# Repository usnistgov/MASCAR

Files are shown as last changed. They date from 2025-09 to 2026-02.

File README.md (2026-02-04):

# MASCAR
Assets and codebase for the Multi-Agent Synchronized Collaborative Assembly Replication (MASCAR) testbed.  This testbed was developed by the Collaborative Robotics Lab at the National Institute of Standards and Technology.

# Overview Video
View here:  https://youtu.be/IEJgwW6c2EQ

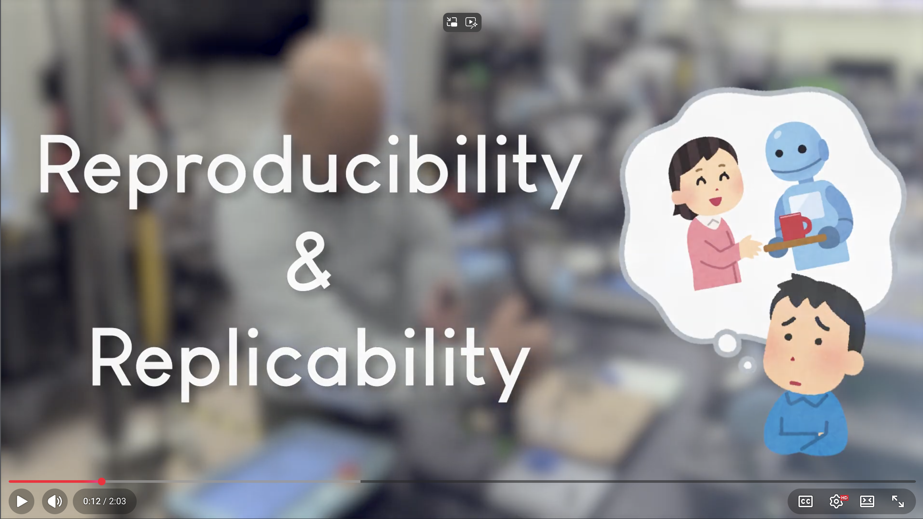
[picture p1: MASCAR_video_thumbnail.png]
MASCAR intro video (http://www.youtube.com/watch?v=IEJgwW6c2EQ "Introduction to MASCAR")


# Documentation
Please see our short paper in HRI 2026 for an overview:

[Local version](/HRI_2026_LBR%20-%20MASCAR.pdf)

[ACM Digital Library]() - Forthcoming

# Table of Contents
[CAD Files](/CAD%20Files/)
- [Testbed Components](/CAD%20Files/Testbed%20Components/)
    - [Cart and Tabletop](/CAD%20Files/Testbed%20Components/Cart%20and%20Tabletop/) - 
    Contains 2D and 3D models for recreation of the elements of the testbed, including the cart, surface mounting plates, and optical table tabletop design.
    - [Gripper Components](/CAD%20Files/Testbed%20Components/Gripper%20Components/) - Designs for yoke flange attached to the Robotiq 2F-85 for manual positioning and button control
    - [MoCap Marker Plates](/CAD%20Files/Testbed%20Components/MoCap%20Marker%20Plates/) - Models for attaching reflective mocap markers to the camera cold shoe mounts
    - [Raspberry Pi](/CAD%20Files/Testbed%20Components/Raspberry%20Pi/) - RP case models
    - 'NIST - Espressif ESP32-C3-DevKitC Case.stl' - Custom-designed case for ESP32
    - 'Laser_Diode_Holder.step' - 

[Design Documentation](/Design%20Documentation/)
- Diagrams, Bill of Materials, process description, design notes, and other instructions for running components of the testbed

[Safety](/Safety/)
- [Human Subjects Testbed](/Safety/Human%20Subjects%20Testbed/) - SOP for testbed setup & assembly
- [Universal Robots](/Safety/Universal%20Robots/) - Safety Manual for use of the UR3e

[Source Code](/Source%20Code/)
- [Python Code](/Source%20Code/Python%20Code/)) - Contains the code for controlling the Robotiq gripper via Raspberry Pi and UR RTDE, and the logger code for recording robot & gripper states
- [URCaps](/Source%20Code/URCaps/) - URCap program to be installed on UR3 for custom Robotiq gripper control

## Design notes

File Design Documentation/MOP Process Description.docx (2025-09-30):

# Teach-by-Demonstration Pilot Study

# (Pilot Testing Protocol)

Version 1.0

# Overview

This document outlines the process for executing a trial teach-by-demonstration data collection study. The study simulates a human subject trial in which a volunteer goes through the process of controlling a robot and its attached gripper to complete a sample assembly task. While the actual human subject study will leverage the NIST assembly taskboards, this assembly task is simplified to a pick-and-place operation of cubes into a grid. This simplification is for the sake of expediting the time necessary to complete the assembly.

The purpose of this study is to evaluate the efficacy of the testbed setup, data collection, and post-process data alignment and packaging.

# Training the Study Volunteer

Use the attached volunteer overview document to provide a convenient reference guide for the volunteer.

Provide a brief overview of robot safety, including the following points:

- Emergency stops
- Freedrive mode
- Joint limits and automatic deactivation

Provide a brief overview of the data being collected, including the following:

- Video of the volunteer operating the robot
- Point cloud data of the testbed environment, including the volunteer.
- Position and state data from the robot, which includes joint angles, Cartesian coordinates of the gripper, measured forces, etc.
- State data from the gripper, including button presses and aperture of the gripper.
- Screen recordings of the teach pendant.
- Time codes for each of the data streams.

Provide a brief summary of the controls for the robot.

- Demonstrate the gripper actuation
- Demonstrate freedrive mode
- Demonstrate picking up and putting down an object

Allow the study participant to practice controlling the robot and picking up and placing objects within the testbed. Reset the testbed prior to beginning the trial.

# Testbed Setup and Starting the Recording Process

Prior to starting the testing process, set up the staging area with the five cubes. Each cube goes into a specific slot on the staging area fixture:

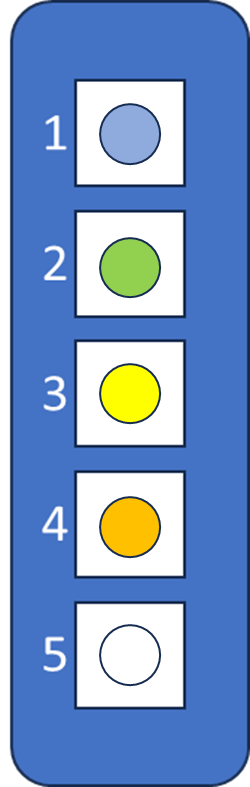
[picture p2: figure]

Blue: Slot 1 Green: Slot 2 Yellow: Slot 3 Orange: Slot 4 White: Slot 5

The 5x5 target grid should be empty of all blocks.

The robot’s J6 should be oriented such that the gripper control flange is pointed to the side with the participant’s dominant hand (left or right).

A second tester must be present to provide emergency services, including being stationed with an emergency stop button to stop the robot in the event of dangerous motions.

# Teach-By-Demonstration Process Description

The volunteer will be instructed to control the robot using the on-arm button interface to pick up and place cubes in a specific order.

When the participant is ready, start recording for all data streams.

For each pick-and-place operation, provide a card stating which cube is to be picked up, and the 2-digit location of the target receptacle of the block. Give the participant only one card at a time, and provide the next card only after the current object has been placed.

# Teach-by-Demonstration Pilot Study

# (Volunteer Reference Sheet)

# Safety

Before beginning the test, please familiarize yourself with the safety functions of the robotic testbed.

An emergency stop button (large red button with an orange and black base) is provided for your benefit. If at any time the robot or its actions make you feel unsafe, press the red button and the robot will stop immediately. Stopping the robot in this manner requires a manual restart (the button must be manually released, and the robot re-enabled to allow it to move again), so it is impossible for the robot to automatically restart itself.

During the trials, one of the testers will also be watching the robot’s actions, and will have their own, separate emergency stop button. This tester’s singular responsibility is to ensure your safety.

The robot also constantly monitors its functional state, and will disable itself if aberrant actions are detected. Aberrant actions include:

- Moving faster than a set, maximum speed,
- Rapid acceleration (including impacts)
- Excessive force, and
- Encountering physical joint limits (the robot’s joints cannot be turned infinitely due to hardware limitations).
- Encountering virtual position limits (the robot may be configured to prevent it moving beyond certain position thresholds; e.g., attempting to move below the table surface)

While working with the robot, it is recommended you tie back any loose hair or clothing to prevent accidentally being snagged on the robot, its gripper, or the various parts in the testbed. Keep hands, hair, and clothing away from the gripper while it is opening or closing. Although commanded forces have been reduced to prevent injury, it may be startling or slightly uncomfortable if you get pinched.

All sensitive or personal equipment (jewelry, name badges, etc.) should be removed prior to beginning the trial. A bin will be provided to deposit these materials.

# Task Overview

During this study, your task will be to move cubes from a staging area (left column) to specific locations on the target board (right grid). You will be instructed which block to move from the staging area using its numerical position in the column, and where on the grid to move the block using its column and row combination. Each block will have a colored indentation on the top, but this is not relevant to this test.

For example, you may be asked to move block #2 to position E1 on the grid, in which case you will use the robot to pick up the block from the staging area in space 2 (second from the top), and then move it to location E1 (top right square) on the grid. While each block will have a color associated with it, these colors are not part of this test.

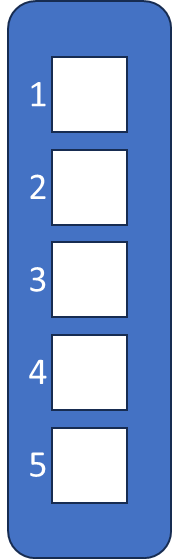
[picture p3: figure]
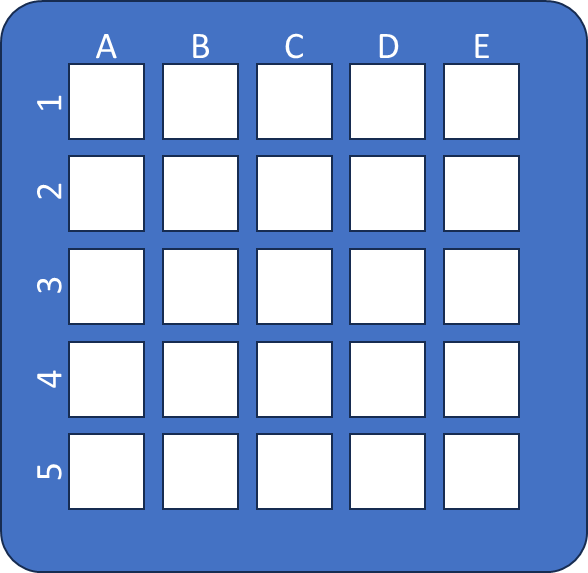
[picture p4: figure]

The order of the pick-and-place operations does matter, so please try to do each action in the order it is given to you.

Note that you will not be allowed to correct erroneous placement of objects. Simply move on to the next object.

The duration of the test will be timed. However, the goal of this test is to evaluate task accuracy, and not to determine how quickly you can complete it.

Additional measurements that will be recorded include:

- Video and audio of the test,
- Point cloud data (i.e., a series of dots in three dimensions that show where the surfaces of people and objects are in the environment)
- Task accuracy as a percentage of maximum number of correct placements, and as a measure of order of operations,
- Robot and gripper joint configurations,
- Gripper location,
- Incurred forces and torques, and
- Button presses

# Robot Controls

For this experiment, you will be controlling the robot manually by means of a button interface attached to the robot’s gripper. The interface consists of a collar attached to the robot, just above a robotic gripper. The protrusion with the buttons is double-sided, and has an identical button layout on the opposite side.

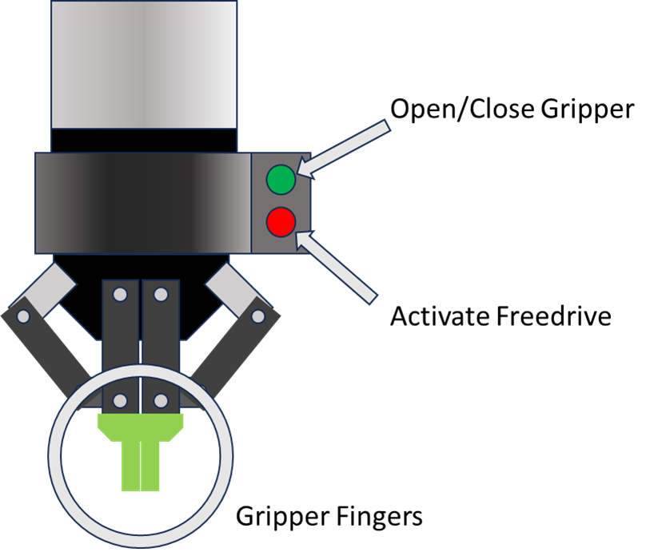
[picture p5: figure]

The top buttons (green) control the gripper, and cycle between “open” (the green “fingers” are spread apart) and “closed” (the green fingers are close together). To actuate the gripper, simply simultaneously press the two green buttons on both sides of the gripper, hold for about half a second, and then release. If the gripper is open, this will close it; and if the gripper is closed, it will open it again.

The bottom buttons (red) enable the robot’s “freedrive” mode. In freedrive mode, the brakes release and the robot will allow you to push and pull it into different joint configurations. While in freedrive mode, the robot is active, and is interpreting the forces you are applying to it as motion commands. Pressing and holding the red buttons will enable freedrive mode. Freedrive mode will remain active while both buttons are pressed. Releasing the buttons will disable freedrive, and the robot’s brakes will engage again.

The following instructions are recommended to ensure smooth operations:

- When using freedrive mode, hold the gripper with both hands to provide the maximum level of control.
- Do not attempt to move the robot quickly. Completion time is not part of this test.

# Teach-by-Demonstration Pilot Study

# (Subject Information and Informed Consent Form)

A sample test methodology for subject data collection as part of a new research testbed for human-robot interaction.

Qualified investigator: Megan Zimmerman

Sub-investigator(s): Jeremy Marvel and Shelly Bagchi

Introduction:

You are being invited to participate in a research study (also known as a “test” or “trial”). This research is part of a pilot, and will focus on the collection of data for the verification and validation of a testing methodology and is not part of a larger human subject study. The data collected will be used to evaluate and calibrate the processes for disparate data stream synchronization and alignment.

Including the time necessary to explain the purpose of this study (including training, reading the reference materials and this consent form, and conducting the teach-by-demonstration trial) is expected to take no longer than 30 minutes.

It is your choice if you want to participate in this study.

This form explains why we are conducting this study, the nature of the data being collected, and how this data is being stored and protected.

What is the purpose of this study?

The purpose of this study is to generate test data for the evaluation of the methodologies of data collection, data synchronization, and automated data segmentation and analysis. The research questions being addressed are:

Are the processes of collecting data accurate and repeatable?

What is the uncertainty of the data alignment methodology?

Is the collection of sensors meaningful for the evaluation of human-robot interaction?

Who can take part in this study?

To take part in this study, you must be at least 18 years of age, be able to see objects in the environment with or without visual aids, have full functionality of at least one arm and hand, and be able to listen to and understand instructions presented in English.

What will we ask you to do?

You will be trained to use an industrial robot with a simplified interface to simulate a teach-by- demonstration programming process. Following this, you will be asked to complete a series of five (5) pick-and-place operations using a small industrial robot, guided by hand, with a robotic gripper controlled using buttons attached to the robot. You will be instructed on the order of the objects to pick up, and where to place them on a grid.

Risks and discomforts

Physical risk: The robot and its gripper are controlled manually and at a reduced speed. It is possible, however, that study participants could get pinched by the gripper or caught between the robot and the test surface. Minor bruising may be possible under such circumstances.

Security risk: This pilot study includes the use of video equipment with which the face or other personally identifiable physical features of the participant may be recorded. All data collected during this study will be securely stored on a password-protected drive, and are to be used only for internal purposes (i.e., no data containing personally-identifiable information will be publicly released).

Benefits

Participation in this study will produce valuable data that will be used to validate and fine-tune the testing protocols, that will, in turn, be used as bases for establishing standards for human-robot interaction research as part of the IEEE P3108 committee on recommended practices for human-robot interaction.

If you have questions

If you have any questions following this study, or would like to know more about the resulting collected data, please contact Megan Zimmerman, Computer Scientist in the NIST Intelligent Systems Division. You may ask questions now, or contact Megan at megan.zimmerman@nist.gov. You may also request a copy of this consent form by contacting Megan at the above address.

Statement of Consent

I have read the above information, and have received answers to any questions I asked. I consent to take part in the study and have my likeness recorded for the purpose of test protocol verification.

Your Signature: ____________________________________________

Your Name (printed): _________________________________________

Date: _____________________________________

Signature of person obtaining consent: ____________________________________________

Printed name of person obtaining consent: _________________________________________

Date: _____________________________________

This consent form will be kept by the researcher for at least three (3) years beyond the end of the study.

# Teach-by-Demonstration Pilot Study

# (Testing Scenarios)

# Scenario 1:

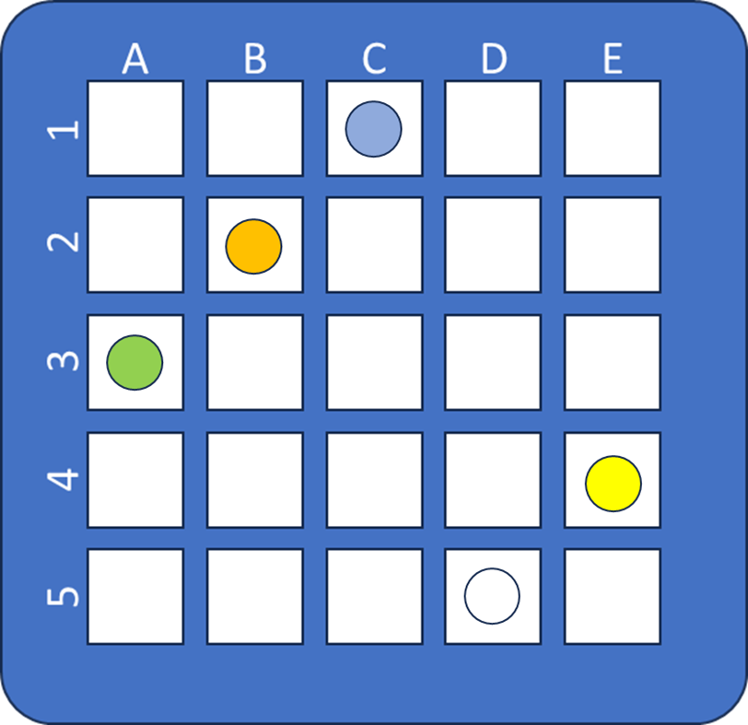
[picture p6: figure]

| Block
| 1 | 2 | 3 | 4 | 5
Target Location | C1 | A3 | E4 | B2 | D5

# Scenario 2:

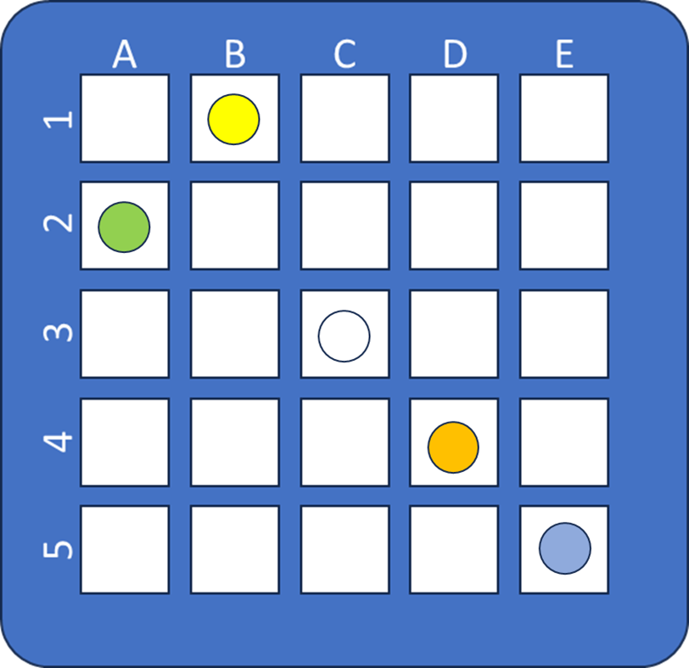
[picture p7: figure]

| Block
| 1 | 2 | 3 | 4 | 5
Target Location | E5 | A2 | B1 | D4 | C3

# Scenario 3:

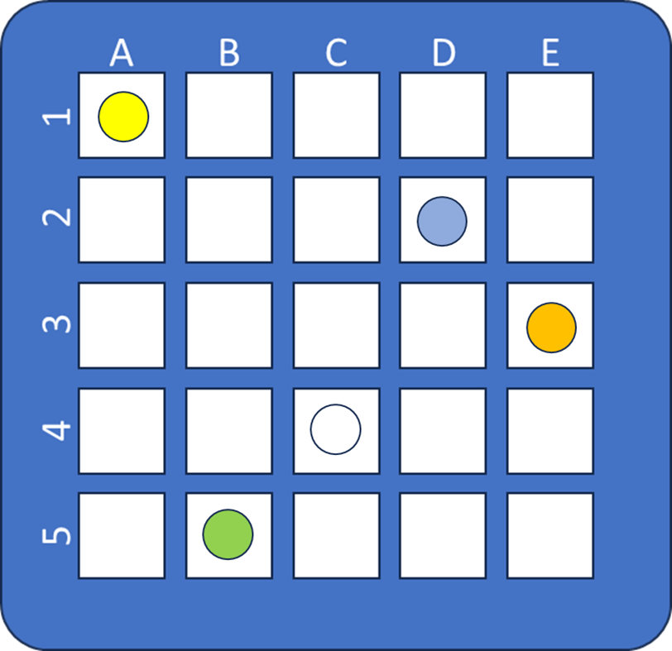
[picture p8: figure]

| Block
| 1 | 2 | 3 | 4 | 5
Target Location | D2 | B5 | A1 | E3 | C4

# Scenario 4:

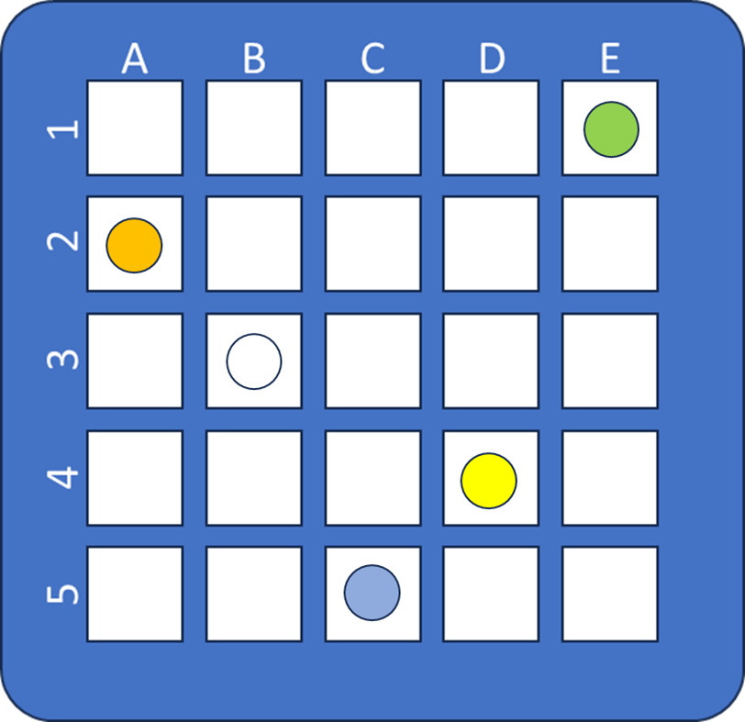
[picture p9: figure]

| Block
| 1 | 2 | 3 | 4 | 5
Target Location | C5 | E1 | D4 | A2 | B3

# Scenario 5:

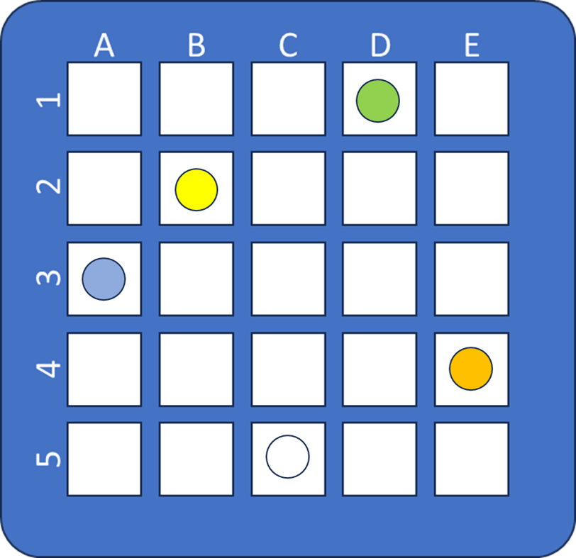
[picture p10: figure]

| Block
| 1 | 2 | 3 | 4 | 5
Target Location | A3 | D1 | B2 | E4 | C5

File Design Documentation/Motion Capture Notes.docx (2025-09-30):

Motion Capture SOP Notes

OptiTrack Duo and Trio

If the intrinsic calibration of the cameras is not loading correctly (e.g., if the cameras appear to be co-located, or are not triangulating markers correctly), it can be manually forced to load using the following steps:

With the camera powered on and connected to the computer via USB:

- From the “Edit” menu, select “Reset Settings.” This will force a reload of the camera definition, effectively placing the cameras in the approximate correct position.
- Then, in the “Ground Plane” window, select “Change Ground Plane” and then in the ground plane editing window, select “Reset.” This will force the intrinsic calibration to reload, correcting any potential errors in camera offsets and orientations.

To set the ground plane and define the origin of the coordinate space:

Using three retroreflective markers, create an “L” shape pattern on the surface of the ground plane. The long segment of the “L” defines the positive Z axis, and the short segment defines the positive X axis

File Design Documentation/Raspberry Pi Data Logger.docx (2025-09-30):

Raspberry Pi 2B

Button: 1 lead to GPIO, 1 to GND

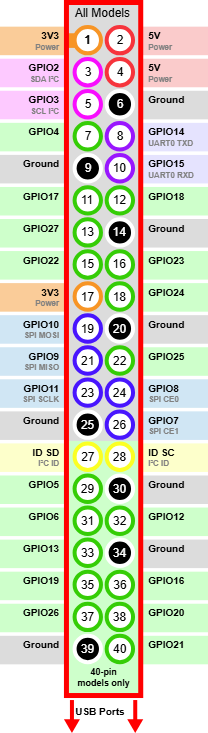
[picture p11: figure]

Raspberry Pi 5

1x USB3.0 port: SSD for data output

1x USB2.0 port: Audio in for timecode generator

1x RJ45 Ethernet port to connect to LAN for access to UR3e & Gripper server

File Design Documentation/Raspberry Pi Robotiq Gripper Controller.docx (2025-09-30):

# Raspberry Pi Control of Robotiq Grippers

Version 1.0

23 April, 2025

Last edited by: Jeremy Marvel (jeremy.marvel@nist.gov)

# Introduction

This transcript documents the process for setting up a Raspberry Pi as a remote triggering device for opening and closing a Robotiq gripper. The original intention of this process was to enable manual control of the gripper using a simple button press. The source code registers any button press longer than 0.5s as a “press event” to prevent unintentional actuation, and each press event will alternatively open and close the gripper.

The methods described in this document have been tested on both the 3-fingered Modbus Ethernet gripper, as well as the 2-fingered RS485 serial gripper.

# Bill of Materials

NOTE: Bill of Materials does not include the cost of the gripper or associated cables. Instead, it reflects only the materials needed to control the gripper with a Raspberry Pi.

Item | Quantity | Example Link & Cost
Raspberry Pi 3B | 1 | $35.00 (https://www.adafruit.com/product/3055)
4GB MicroSD Card | 1 | $8.49 (https://www.amazon.com/SanDisk-microSDHC-Memory-SDSDQ-004G-Packaging/dp/B00FM1JGHK/?th=1)
Normally-open momentary switch | 1 | $8.99 (package of 20) (https://www.amazon.com/MTDELE-Momentary-Button-Switch-Normally/dp/B0D7ZYZN58/)
24VDC 10A power supply | 1 | $22.99 (https://www.amazon.com/ALITOVE-Transformer-Universal-Regulated-Switching/dp/B078RYWZMH?th=1)
5V 3A micro USB power supply (for the Raspberry Pi) | 1 | $9.99 (https://www.amazon.com/Listed-iUniker-Raspberry-Supply-Switch/dp/B0B79FVPQ4/)
22 Gauge wire (for wiring the button) | 2 spools | $15.20 (package of 2) (https://www.amazon.com/BINNEKER-Gauge-Electric-Tinned-Copper/dp/B0B19HJFPX/?th=1)
Network switch | 1 | $13.95 (https://www.amazon.com/Ethernet-Splitter-Optimization-Unmanaged-TL-SG105/dp/B00A128S24?th=1)
RJ45 CAT5 Network Cable | 1 | $9.99 (https://www.amazon.com/Cable-Matters-Snagless-Ethernet-Black/dp/B007NZGPAY/?th=1)

OR
USB to RS485 adapter | 1 | $15.35 (https://www.amazon.com/Industrial-USB-RS485-Converter-Communication/dp/B081MB6PN2/)
Modbus Ethernet | | $124.60
USB to RS485 | | $116.01

# Wiring a Button to a Raspberry Pi

For this setup, we use normally open (NO) momentary switches, with one lead connected to the GPIO pin 2 on the Raspberry Pi, and the other lead connected to the GND pin. For the NIST application, two NO momentary switches were wired in series to force the operator to press and hold both buttons for 0.5s to trigger the gripper actuation.

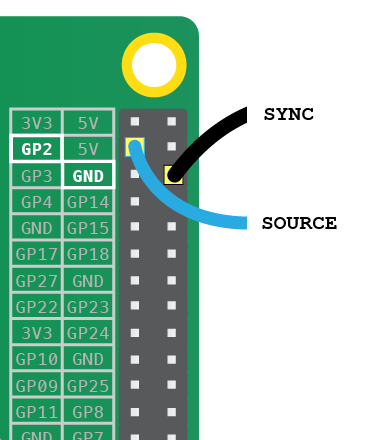
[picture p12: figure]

# Modbus over Ethernet (Robotiq 3-Finger Gripper)

Installation of the Python libraries

python3 -m pip config set global.break-system-packages true

python3 -m pip install pyModbusTCP

SOURCE

from pyModbusTCP.client import ModbusClient

from gpiozero import Button

import time

import threading

import warnings

class GripperController:

def __init__(self, server_ip, port=502, unit_id=9, update_interval=0.1):

# Initialize Modbus client and update thread

self.client = ModbusClient(host=server_ip, port=port, auto_open=True, unit_id=unit_id)

self.client.open()

self.update_interval = update_interval

self._running = True

self._thread = threading.Thread(target=self._update_loop)

self._thread.start()

def _update_loop(self):

"""Continuously update gripper status."""

while self._running:

self._update_status()

time.sleep(self.update_interval)

def _update_status(self):

"""Update and store the gripper status from Modbus server."""

readData = self.client.read_input_registers(0,8)

if readData:

self.gSTA, self.gIMC, self.gGTO, self.gMOD, self.gACT, self.gDTS, self.gDTC, self.gDTB, self.gDTA = self.stat(self.add_leading_zeros(bin(readData[0])))

self.FaultStatus, self.FingerA_PositionReqEcho = self.Byte_status(self.add_leading_zeros(bin(readData[1])))

self.FingerA_Position, self.FingerA_Current = self.Byte_status(self.add_leading_zeros(bin(readData[2])))

self.FingerB_PositionReqEcho, self.FingerB_Position = self.Byte_status(self.add_leading_zeros(bin(readData[3])))

self.FingerB_Current, self.FingerC_PositionReqEcho = self.Byte_status(self.add_leading_zeros(bin(readData[4])))

self.FingerC_Position, self.FingerC_Current = self.Byte_status(self.add_leading_zeros(bin(readData[5])))

self.Scissor_PositionReqEcho, self.Scissor_Position = self.Byte_status(self.add_leading_zeros(bin(readData[6])))

self.Scissor_Current, RES = self.Byte_status(self.add_leading_zeros(bin(readData[7])))

else:

print("Error reading data in update_status.")

@staticmethod

def add_leading_zeros(bin_num, total_length=16):

"""Ensure binary number string has correct number of digits."""

bin_str = str(bin_num)[2:] # remove '0b' prefix

return bin_str.zfill(total_length)

@staticmethod

def Byte_status(variable: int) -> str:

"""Split and parse byte status."""

B1 = int(variable[0:8],2)

B2 = int(variable[8:16],2)

return B1, B2

@staticmethod

def stat(variable: int) -> str:

"""Split and parse status."""

# Define gripper modes

modes = ["Basic Mode", "Pinch Mode", "Wide Mode", "Scissor Mode"]

# Split and parse status bits

gSTA = int(variable[0:2],2)

gIMC = int(variable[2:4],2)

gGTO = int(variable[4],2)

gMOD = int(variable[5:7],2)

gMOD = modes[gMOD] # Translate mode code to string

gACT = int(variable[7],2)

gDTS = int(variable[8:10],2)

gDTC = int(variable[10:12],2)

gDTB = int(variable[12:14],2)

gDTA = int(variable[14:16],2)

return gSTA, gIMC, gGTO, gMOD, gACT, gDTS, gDTC, gDTB, gDTA

def activate(self):

"""Activate the gripper."""

# response = self.client.write_multiple_registers(0, [self._action_req_variable(rACT=1), 0, 0])

self.client.write_multiple_registers(

0,

[self._action_req_variable(rACT=1, rGTO=1, rMOD=0, rICF=0),

self._position_req_variable(0),

self._write_req_variable(0, 0)]

)

print("Gripper activate")

time.sleep(1)

def command_gripper(self, rPRA=[1, 1, 1], rSP=[250, 250, 250], rFR=[250, 250, 250], rMOD="Basic", rICF=False):

"""Send a command to the gripper."""

# self.status()

modes = {"Basic": 0, "Pinch": 1, "Wide": 2, "Scissor": 3}

rMOD = modes[rMOD]

if rICF:

for var in [rPRA, rSP, rFR]:

if isinstance(var, int):

self.close()

raise ValueError("Input variables must be 3d vectors when using Individual Control Flag.")

response = self.client.write_multiple_registers(

0,

[self._action_req_variable(rACT=1, rGTO=1, rMOD=rMOD, rICF=1),

self._position_req_variable(rPRA[0]),

self._write_req_variable(rSP[0], rFR[0]),

self._write_req_variable(rPRA[1],rSP[1]),

self._write_req_variable(rFR[1],rPRA[2]),

self._write_req_variable(rSP[2], rFR[2]),]

)

else:

for var in [rPRA, rSP, rFR]:

if isinstance(var, list):

warnings.warn("only first value of 3d vector will be used when not using Individual Control Flag.")

response = self.client.write_multiple_registers(

0,

[self._action_req_variable(rACT=1, rGTO=1, rMOD=rMOD, rICF=0),

self._position_req_variable(rPRA[0]),

self._write_req_variable(rSP[0], rFR[0])]

)

def status(self):

readData = self.client.read_input_registers(0,8)

if readData:

self.gSTA, self.gIMC, self.gGTO, self.gMOD, self.gACT, self.gDTS, self.gDTC, self.gDTB, self.gDTA = self.stat(self.add_leading_zeros(bin(readData[0])))

self.FaultStatus, self.FingerA_PositionReqEcho = self.Byte_status(self.add_leading_zeros(bin(readData[1])))

self.FingerA_Position, self.FingerA_Current = self.Byte_status(self.add_leading_zeros(bin(readData[2])))

self.FingerB_PositionReqEcho, self.FingerB_Position = self.Byte_status(self.add_leading_zeros(bin(readData[3])))

self.FingerB_Current, self.FingerC_PositionReqEcho = self.Byte_status(self.add_leading_zeros(bin(readData[4])))

self.FingerC_Position, self.FingerC_Current = self.Byte_status(self.add_leading_zeros(bin(readData[5])))

self.Scissor_PositionReqEcho, self.Scissor_Position = self.Byte_status(self.add_leading_zeros(bin(readData[6])))

self.Scissor_Current, RES = self.Byte_status(self.add_leading_zeros(bin(readData[7])))

else:

print("Error reading data in status.")

def _action_req_variable(self, rARD: int = 0, rATR: int = 0, rGTO: int = 0, rACT: int = 0, rMOD:int = 0, rICS:int = 0, rICF:int = 0 ) -> str:

"""Build action request variable."""

# Check if the input variables are either 0 or 1

for var in [rARD, rATR, rGTO, rACT]:

if var not in [0, 1]:

raise ValueError("Input variables must be either 0 or 1.")

rMOD = bin(rMOD).replace("0b", "").zfill(2)

# Construct the string variable

string_variable = f"0b00{rARD}{rATR}{rGTO}{rMOD}{rACT}0000{rICS}{rICF}00"

return int(string_variable,2)

def _position_req_variable(self, rPR: int = 0) -> str:

"""Build position request variable."""

# Check if the input variables are between 0 or 255

for var in [rPR]:

if var not in range(0,256):

raise ValueError("Input variables must be between 0 and 255.")

rPR = format(rPR, '08b')

# Construct the string variable

string_variable = f"0b00000000{rPR}"

return int(string_variable,2)

def _write_req_variable(self, X: int = 0, Y: int = 0) -> str:

"""Build write request variable."""

# Check if the input variables are between 0 to 255

for var in [X, Y]:

if var not in range(0,256):

raise ValueError("Input variables must be between 0 and 255.")

X = format(X, '08b')

Y = format(Y, '08b')

# Construct the string variable

string_variable = f"0b{X}{Y}"

return int(string_variable,2)

def close(self):

"""Stop the update thread and close the Modbus client."""

self._running = False

self._thread.join()

self.client.close()

print("Connection closed.")

# @brief Main program loop

def main():

# Create and activate gripper controller

while ([gripper.FingerA_Position, gripper.FingerB_Position, gripper.FingerC_Position] != target_position):

print(f"FingerA_Position: {gripper.FingerA_Position}")

print(f"FingerA_Position: {gripper.FingerA_Position}")

gripper = GripperController("169.254.116.11")

gripper.activate()

individual_control = False

target_position = [255, 255, 255] # Desired finger positions

speed = [250, 205, 250] # Speed of the movement

force = [250, 250, 250] # Force applied by the fingers

target_position = [target_position[0]] * 3 if not individual_control else target_position

startTime_ = time.perf_counter()

stopTime_ = time.perf_counter()

state = False

time.sleep (0.2)

# Send command to gripper and wait for it to reach final position

target_position = [255, 255, 255]

gripper.command_gripper(rPRA=target_position, rSP=speed, rFR=force, rICF=individual_control)

button = Button(2)

while True:

button.wait_for_press()

startTime_ = time.perf_counter()

button.wait_for_release()

stopTime_ = time.perf_counter()

elapseTime_ = stopTime_ - startTime_

if elapseTime_ > 0.5:

state = not state

if state:

target_position = [0, 0, 0]

else:

target_position = [0, 0, 0]

gripper.command_gripper(rPRA=target_position, rSP=speed, rFR=force, rICF=individual_control)

if __name__ == "__main__":

main()

There are two known issues regarding the use of the Raspberry Pi4B for communicating with the Robotiq grippers over Ethernet; one is a hardware issue, and the other is an OS setting issue when running Raspian based on the Debian GNU/Linux 12 (Bookworm) kernel.

Hardware Issue:

The Pi4B requires an Ethernet cable with all 8 pins of the RJ45 plug connected and wired accordingly.

OS Setting Issue:

By default, the Raspberry Pi4B requires a router that can either set DHCP IP addresses, or “confirm” the static IP address of the Pi. Even if you set a static IP address, the OS will keep “trying” to establish a connection with the LAN, despite that it is visible to other machines on the LAN and can likewise see those other machines. Eventually the OS times out on establishing this connection, and disables the RJ45 port until a new connection is detected.

To bypass this verification step for a static IP address, use the following instructions:

Setting a static IP address (Network Settings (icon on the top-right corner of the desktop) → Advanced Options → Edit Connections)

- Double-click “Wired connection 1”
- Under the “General” tab
  - Set “Connect automatically with priority” to 100 (default is -999)
  - Set “Metered connection” to No
- Under “IPv4 Settings” tab
  - Set “Method” to Manual
  - Add a new static IP address and netmask based on the LAN you are setting up
  - Make sure “Require IPv4 addressing for this connection to complete” is NOT checked (otherwise OS will eventually shut it off since a network switch/hub will not provide verification of IP address)
- Under “IPv6 Settings” tab
  - Set “Method” to Disabled
- Click “Save” button and exit

# USB to RS485 Serial (Robotiq 2-Finger Gripper)

Controlling the 2-finger Robotiq gripper is substantially easier, as communications between the Raspberry Pi and the gripper is handled via an RS485 interface.

Installation of the Python libraries

python3 -m pip config set global.break-system-packages true

python3 -m pip install pyRobotiqGripper

python3 -m pip install minimalmodbus

Wiring and Installation

From the Robotiq documentation:

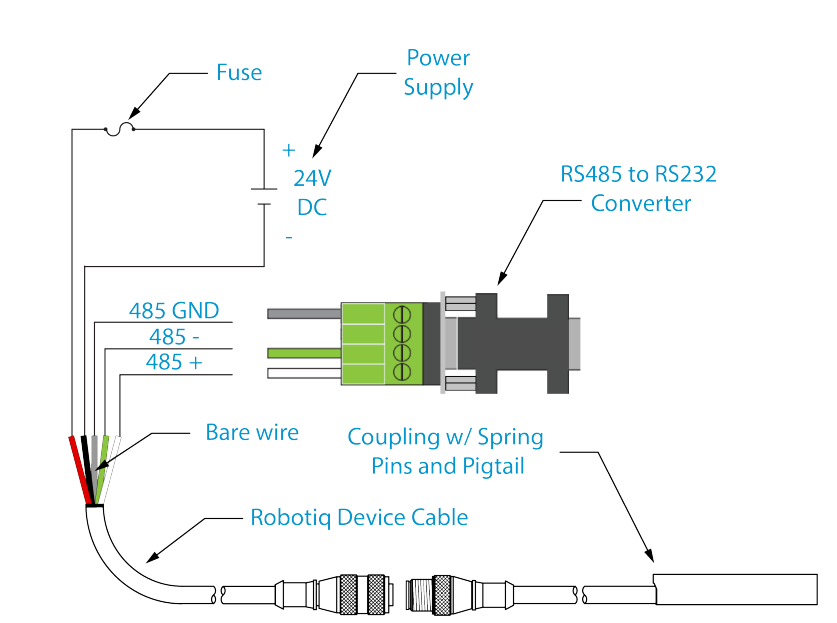
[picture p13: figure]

Our configuration did not use an RS232 - RS485 converter, but instead used a USB - RS485 adapter. The wiring at the RS485 side remained the same.

SOURCE

from gpiozero import Button

import pyRobotiqGripper

import time

# @brief Main program loop

def main():

gripper = pyRobotiqGripper.RobotiqGripper()

gripper.activate()

startTime_ = time.perf_counter()

stopTime_ = time.perf_counter()

state = False

time.sleep (0.2)

gripper.close()

button = Button(2)

while True:

button.wait_for_press()

startTime_ = time.perf_counter()

button.wait_for_release()

stopTime_ = time.perf_counter()

elapseTime_ = stopTime_ - startTime_

if elapseTime_ > 0.5:

state = not state

if state:

gripper.open()

else:

gripper.close()

if __name__ == "__main__":

main()

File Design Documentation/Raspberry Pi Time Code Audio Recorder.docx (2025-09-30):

# Recording Time Code Generator Audio using a Raspberry Pi

Version 1.0

23 August, 2025

Last edited by: Jeremy Marvel (jeremy.marvel@nist.gov)

Installation of the Python library

python3 -m pip install pyaudio

https://people.csail.mit.edu/hubert/pyaudio/docs/

PyAudio library

https://people.csail.mit.edu/hubert/pyaudio/docs/

# @brief Launch and run in a new thread the audio recorder

# =============================================================================================================

def timecode_recorder():

form_1 = pyaudio.paInt16 #! 16-bit resolution

chans = 1 #! 1 channel

samp_rate = 44100 #! 44.1 kHz sampling

chunk = 4096 #! 4k samples for buffer

global running_

global recording_

global timestr_

global index_

global timeRec_

#! Create the Python audio instantiation

audio = pyaudio.PyAudio()

print ("Opening audio on device index " + str(index_))

stream = audio.open(format = form_1, rate = samp_rate, channels = chans,\

input_device_index = index_, input = True, \

frames_per_buffer = chunk)

stream.stop_stream()

stream.close()

#! Loop until told by the main program function to quit

while running_:

if recording_:

timeRec_ = True

print ("Recording time code data")

stream = audio.open(format = form_1, rate = samp_rate, channels = chans,\

input_device_index = index_, input = True, \

frames_per_buffer = chunk)

wavfilename = timestr_ + "_audio.wav"

frames = []

#! Loop until told by the main program function to stop recordng

while recording_:

data = stream.read(chunk)

frames.append(data)

print ("Finalizing time code data log")

stream.stop_stream()

stream.close()

wavfile = wave.open(wavfilename, 'wb')

wavfile.setnchannels(chans)

wavfile.setsampwidth(audio.get_sample_size(form_1))

wavfile.setframerate(samp_rate)

wavfile.writeframes(b''.join(frames))

wavfile.close()

print("Finished writing timecode file")

timeRec_ = False

print("Timecode recorder quitting...")

audio.terminate()

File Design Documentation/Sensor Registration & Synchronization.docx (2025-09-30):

Calibration

Sensor | Intrinsic Calibration | Extrinsic Calibration
Camcorder | N/A | Coordinate space registration using an artifact with OptiTrack markers. Sensor uses a custom routine to track an object in its intrinsic coordinate system, while the OptiTrack tracks the pose of the sensor and the artifact. Calculate the transformation from the sensor’s coordinate space to the OptiTrack coordinate space using the NIST registration method.
Intel RealSense | Pre-calibrated | Coordinate space registration using an artifact with OptiTrack markers. Sensor uses a custom routine to track an object in its intrinsic coordinate system, while the OptiTrack tracks the pose of the sensor and the artifact. Calculate the transformation from the sensor’s coordinate space to the OptiTrack coordinate space using the NIST registration method.
Audio | N/A | OptitTrack marker
Captury MoCap | Built-in setup routine per camera | Built-in setup routine between cameras and with the measurement space
OptiTrack MoCap | Pre-calibrated | N/A; Built-in setup routine with the measurement space.
Vicon MoCap | Built-in setup routine per camera | Built-in setup routine between cameras
UR Teach Pendant | Occasional confirmation of robot pose on startup | N/A currently (Probably could put on OptiTrack markers)
Forge/OS Teach Pendant | N/A | N/A currently (Probably could put on OptiTrack markers)
UR UR3e robot | DH parameters; built-in calibration routine at startup | Intrinsic design of the testbed mounting points
Robotiq robotic gripper | Built-in calibration routine at startup | Manual TCP offset on teach pendant
Control collar | N/A | N/A currently

Registration

Sensor | Data Format | Spatial Registration | Temporal Synchronization
Camcorder | AVI video and embedded 2-channel audio | Attached OptiTrack marker | Time code generator
Intel RealSense | | Attached OptiTrack marker
Audio | WAV | Attached OptiTrack marker | Time code generator
Captury MoCap | AVI video and tracking data | Modification of the calibration target to include MoCap markers to register with the OptiTrack and/or Vicon
OptiTrack MoCap | Tracking data
Vicon MoCap | Tracking data
UR Teach Pendant | AVI video
Forge/OS Teach Pendant | AVI video
UR UR3e robot | RTDE data stream
Robotiq robotic gripper | | Physically attached to the UR3e tool flange
Control collar | | Physically attached to the Robotiq gripper

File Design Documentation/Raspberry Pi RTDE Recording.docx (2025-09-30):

# Recording Universal Robot Manipulator State Via the RTDE on a Raspberry Pi

Version 1.0

15 August, 2025

Last edited by: Jeremy Marvel (jeremy.marvel@nist.gov)

Guide is available at https://www.universal-robots.com/articles/ur/interface-communication/real-time-data-exchange-rtde-guide/

Download latest release from https://www.github.com/UniversalRobots/RTDE_Python_Client_Library/releases

Installation of the Python library:

python3 -m pip config set global.break-system-packages true

python3 -m pip install ./rtde-<version>-release.zip

# @brief Launch and run in a new thread the UR RTDE recorder

# ======================================================================

def rtde_recorder():

global running_

global recording_

global timestr_

global UR3Rec_

verbose = True

host = "169.254.152.41" #! TODO: Replace with IP address of UR controller

port = 30004

freq = 125

binary = False

if verbose:

logging.basicConfig(level=logging.INFO)

conf = rtde_config.ConfigFile("logger.xml")

output_names, output_types = conf.get_recipe("out")

#! Connect to the robot controller

con = rtde.RTDE(host, port)

con.connect()

#! Get controller version

con.get_controller_version()

#! Set up recipes

if not con.send_output_setup(output_names, output_types, frequency=freq):

logging.error("Unable to configure output")

sys.exit()

#! Start data synchronization

if not con.send_start():

logging.error("Unable to start synchronization")

sys.exit()

writeModes = "wb" if binary else "w"

while running_:

if recording_:

rtdefilename = timestr_ + "_rtde.csv"

rtdetimefile = timestr_ + "_rtde_timestamps.csv"

with open (rtdetimefile, writeModes) as rtdetime:

with open(rtdefilename, writeModes) as csvfile:

writer = None

UR3Rec_ = True

if binary:

writer = csv_binary_writer.CSVBinaryWriter(csvfile, output_names, output_types)

else:

writer = csv_writer.CSVWriter(csvfile, output_names, output_types)

print ("Recording UR3 state data")

writer.writeheader()

#! Loop until instructed to stop by the main program

while recording_:

try:

#state = con.receive_buffered(binary)

state = con.receive(binary) #! Only get the most recent message

if state is not None:

timstr = datetime.datetime.now()

writer.writerow(state)

rtdetime.writerow(timestr)

except rtde.RTDEException:

con.disconnect()

sys.exit()

UR3Rec_ = False

print("Finished writing UR3 log file")

# with open(rtdefilename, writeModes) as csvfile

#! with open() automatically closes the file when completed

# with open (rtdetimefile, writeModes) as rtdetime:

print ("Finalizing UR3 timestamp log")

# while running_

#! Close the connection to the robot controller

con.send_pause()

con.disconnect()

# ======================================================================

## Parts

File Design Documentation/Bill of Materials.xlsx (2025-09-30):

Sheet: Master
 | Cost
Hardware | $51764.27
Robot Control Handle | $34.55
ForgeOS Modifications | $78.43
Computers | $41152.63
Markerless Motion Capture | $33273.62
RPi Gripper Controller | $151.67
RPi Robot Logger | $88.49
Sensors | $9324.57
Task Boards | 0
Total | $135868.23

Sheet: Hardware
Part number | Item description | Link | Cost per unit | Quantity | Total | Note | Total cost: | $51764.27
UR3-e | Universal Robot UR3-E robot with 3kg lift capacity |  | $26995.00 | 1 | $26995.00
Forge/OS | Robot controller interface with multi-robot support |  | $9750.00 | 1 | $9750.00
2-finger adaptive gripper | Robotiq 85mm adaptive, 2-finger gripper for UR e-series robots |  | $5885.00 | 1 | $5885.00
Table base | Wheeled workbench base with hand-crank for height adjustment | https://www.mcmaster.com/3517T81/ | $1771.25 | 1 | $1771.25
Table top V1 | 1/2" thick plywood sheet, painted green, with a self-leveling epoxy finish to provide a level surface | https://www.homedepot.com/p/ProWood-1-2-in-x-2-ft-x-4-ft-BCX-Sanded-Plywood-109119/202093833 | $21.23 | 1 | $21.23 | Price reflects only cost of the plywood sheet, and does not include the paint or epoxy resin
Table top V2 | Machined aluminum table top with 6mm tapped holes for attaching parts and a pre-drilled mounting pattern for the e-series robot |  | $4912.00 | 1 | $4912.00 | Machined at the NIST shops. Price reflects material and labor costs.
Table top V3 | Machined aluminum table top with 6mm tapped holes for attaching parts and a pre-drilled mounting pattern for the e-series robot |  |  | 1 | $0.00 | Machined at the NIST shops. Price reflects material and labor costs.
Rack cabinet | 8U equipment rack cabinet | https://www.bhphotovideo.com/c/product/1260039-REG/auray_ers_8u_ers_8u_steel_equipment.html (https://gcc02.safelinks.protection.outlook.com/?reserved=0) | $139.95 | 1 | $139.95
Shelf material |  |  |  | 2 | $0.00
Shelf support |  |  |  | 3 | $0.00
GFW-ID-CREATORTREE | A/V armatures | https://www.bhphotovideo.com/c/product/1657199-REG/gator_gfw_id_creatortree_frameworks_id_series_all_in_one.html (https://gcc02.safelinks.protection.outlook.com/?reserved=0) | $208.41 | 2 | $416.82
Ergotron 24206214 | Computer cart | https://www.bhphotovideo.com/c/product/1128696-REG/ergotron_neo_flex_24_206_214_lcd_cart.html (https://gcc02.safelinks.protection.outlook.com/?reserved=0) | $1075.00 | 1 | $1075.00
JB01741 | Tablet mount | https://www.bhphotovideo.com/c/product/1675875-REG/joby_jb01741_griptight_tablet_pro_2.html (https://gcc02.safelinks.protection.outlook.com/?reserved=0) | $48.66 | 1 | $48.66
955-000005 | Table-mounted camera stand | https://www.bhphotovideo.com/c/product/1585609-REG/mevo_mv3_11a_bl_table_stand.html (https://gcc02.safelinks.protection.outlook.com/?reserved=0) | $65.99 | 1 | $65.99
Neewer C-Stand with Extension Arm |  | Neewer C-Stand with Extension Arm 66600020 B&H Photo Video (https://www.bhphotovideo.com/c/product/1732647-REG/neewer_66600020_pure_metal_pro_reflector.html) | $102.34 | 5 | $511.70
Sandbags | Neewer Heavy-Duty Sandbags for Light Stands, Boom Stands & Tripods (6-Pack) | Neewer Heavy-Duty Sandbags for Light Stands, Boom Stands (https://www.bhphotovideo.com/c/product/1732696-REG/neewer_66600134_dual_handle_sandbag_6_pack.html) | $25.47 | 1 | $25.47
 |  |  |  | 10 | $0.00
Floor cable trays | Cable Concealment Ramp Track | Auray CBR-1039 Cable Concealment Ramp Track CBR-1039 B&H Photo (https://www.bhphotovideo.com/c/product/1585966-REG/auray_cbr_1039_cable_concealment_ramp_10.html) | $29.24 | 5 | $146.20
 |  |  |  |  | $0.00
 |  |  |  |  | $0.00
 |  |  |  |  | $0.00
 |  |  |  |  | $0.00
1/4-20 to 3/8-16 adapters |  |  |  |  | $0.00
M6 female to M4 male adapter |  |  |  |  | $0.00
 |  |  |  |  | $0.00
 | Light panels |  |  |  | $0.00
 |  |  |  |  | $0.00
 |  |  |  |  | $0.00
 |  |  |  |  | $0.00
 |  |  |  |  | $0.00
 |  |  |  |  | $0.00

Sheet: Robot Control Handle
Part number | Item description | Link | Cost per unit | Quantity | Total | Note | Total cost: | $34.55
 | Normally-open momentary switch | https://a.co/d/glXAlmD | $11.49 | 1 | $11.49
 | Latching switches | https://www.digikey.com/en/products/detail/cw-industries/GPB023B05BR/2235499 | $3.93 | 2 | $7.86
 | Aluminum yoke structure |  | $0.00 | 1 | $0.00 | Raw material. Custom machined at NIST.
 | Handles |  | $0.00 | 1 | $0.00 | 3D printed @NIST
 | 22 Gauge wire (for wiring the button) | https://www.amazon.com/BINNEKER-Gauge-Electric-Tinned-Copper/dp/B0B19HJFPX/?th=1 | $15.20 | 1 | $15.20
 | Sheathing |  | $0.00 | 1 | $0.00
 |  |  | $0.00 | 1 | $0.00
 |  |  |  | 1 | $0.00
 |  |  |  | 1 | $0.00
 |  |  |  |  | $0.00

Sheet: ForgeOS Modification
Part number | Item description | Link | Cost per unit | Quantity | Total | Note | Total cost: | $78.43
 | LVDS to HDMI adapter | https://geekworm.com/products/lvds-to-hdmi-adapter-board-converter-with-lvds-cable?variant=39521988771928 | $35.00 | 1 | $35.00
 | LVDS to HDMI adapter | https://geekworm.com/products/lvds2 | $35.00 | 1 | $35.00
2073-05-40-D-0254-A-4-06-4-T-ND | 40-pin FPC ribbon cable | https://mou.sr/3MWxTQ2 (https://gcc02.safelinks.protection.outlook.com/?url=https%3A%2F%2Fmou.sr%2F3MWxTQ2&reserved=0) | $1.43 | 1 | $1.43
1528-4905-ND | 40-pin FPC ribbon cable to 2x20 IDC adapter | https://mou.sr/47GDsMf (https://gcc02.safelinks.protection.outlook.com/?url=https%3A%2F%2Fmou.sr%2F47GDsMf&reserved=0) | $3.50 | 2 | $7.00
 |  |  |  |  | $0.00
 |  |  |  |  | $0.00
 |  |  |  |  | $0.00
 |  |  |  |  | $0.00
 |  |  |  |  | $0.00
 |  |  |  |  | $0.00
 |  |  |  |  | $0.00
 |  |  |  |  | $0.00
 |  |  |  |  | $0.00
 |  |  |  |  | $0.00
 |  |  |  |  | $0.00
 |  |  |  |  | $0.00
 |  |  |  |  | $0.00
 |  |  |  |  | $0.00
 |  |  |  |  | $0.00
 |  |  |  |  | $0.00
 |  |  |  |  | $0.00
 |  |  |  |  | $0.00
 |  |  |  |  | $0.00
 |  |  |  |  | $0.00
 |  |  |  |  | $0.00
 |  |  |  |  | $0.00
 |  |  |  |  | $0.00
 |  |  |  |  | $0.00
 |  |  |  |  | $0.00
 |  |  |  |  | $0.00
 |  |  |  |  | $0.00
 |  |  |  |  | $0.00
 |  |  |  |  | $0.00

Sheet: Computers and Peripherals
Part number | Item description | Link | Cost per unit | Quantity | Total | Note | Total cost: | $41152.63
Dell Precision 5860 | Desktop computer |  | $12367.78 | 3 | $37103.34
Dell Latitude 7350 | Detachable tablet computer |  | $2315.02 | 1 | $2315.02
 |  |  |  | 1 | $0.00
Monitor |  |  |  | 1 | $0.00
Keyboard |  |  |  | 1 | $0.00
Mouse |  |  |  | 1 | $0.00
BG-UHD-KVM41A | BZBGEAR 4-Port HDMI KVM Switch | https://www.bhphotovideo.com/c/product/1660951-REG/bzbgear_bg_uhd_kvm41a_4x1_kvm_switcher_with.html | $128.00 | 1 | $128.00
Networking switch |  |  |  | 1 | $0.00
Black Lion PG-2 | 120VAC Power conditioner & surge protector |  | $399.00 | 1 | $399.00
USB Audio Line In Adapter |  | https://a.co/d/gPL7H8t | $19.09 | 2 | $38.18
Blackmagic Design ATEM Mini Extreme ISO |  |  | 1169.09 | 1 | 1169.09
 |  |  |  |  | $39983.54

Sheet: Markerless Motion Capture
Part number | Item description | Link | Cost per unit | Quantity | Total | Note | Total cost: | $33273.62
Captury Studio | Software for markerless motion capture |  | $8000.00 | 1 | $8000.00
Netgear M4300-16X | 16-port 10Gb POE Network Switch | https://www.bhphotovideo.com/c/product/1711406-REG/netgear_xsm4316pa_100nes_m4300_16x_stackable_managed_switch.html | $2399.99 | 1 | $2399.99
111297 | 25' 10G network cables | https://www.amazon.com/Monoprice-Entegrade-Cat6a-Ethernet-Patch/dp/B00KWS6VIU/?th=1 | $17.98 | 9 | $161.82
BFS-PGE-13Y3C-C | 1.3 MP POE Color Camera | https://www.edmundoptics.com/p/bfs-pge-13y3c-c-poe-gige-blackflyr-s-color-camera/40198/ | $415.00 | 9 | $3735.00
33-307 | 8mm C-mount lens | https://www.edmundoptics.com/p/8mm-uc-series-fixed-focal-length-lens/41864/ | $260.00 | 9 | $2340.00
 | Modularhose.com purchase |  |  | 1 | $0.00
 |  |  |  | 1 | $0.00
 |  |  |  | 1 | $0.00
 |  |  |  | 1 | $0.00
 |  |  |  |  | $0.00
 |  |  |  |  | $16636.81

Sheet: Raspberry Pi Gripper Controller
Part number | Item description | Link | Cost per unit | Quantity | Total | Note | Total cost: | $151.67
 | Raspberry Pi 3B | https://www.adafruit.com/product/3055 | $35.00 | 1 | $35.00
 | 4GB MicroSD Card | https://www.amazon.com/SanDisk-microSDHC-Memory-SDSDQ-004G-Packaging/dp/B00FM1JGHK/?th=1 | $8.49 | 1 | $8.49
 | 24VDC 10A power supply | https://www.amazon.com/ALITOVE-Transformer-Universal-Regulated-Switching/dp/B078RYWZMH?th=1 | $22.99 | 1 | $22.99
 | 5V 3A micro USB power supply (for the Raspberry Pi) | https://www.amazon.com/Listed-iUniker-Raspberry-Supply-Switch/dp/B0B79FVPQ4/ | $9.99 | 1 | $9.99
 | 22 Gauge wire (for wiring the button) | https://www.amazon.com/BINNEKER-Gauge-Electric-Tinned-Copper/dp/B0B19HJFPX/?th=1 | $15.20 | 1 | $15.20
 | 7 inch touch display for raspberry pi | https://www.digikey.com/en/products/detail/raspberry-pi/SC1227/6152806 | $60.00 | 1 | $60.00
 |  |  |  | 1 | $0.00
 |  |  |  | 1 | $0.00
 |  |  |  |  | $0.00

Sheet: Raspberry Pi Logger
Part number | Item description | Link | Cost per unit | Quantity | Total | Note | Total cost: | $88.49
 | Raspberry Pi 5 | https://www.digikey.com/en/products/detail/raspberry-pi/SC1432/21658257 | $80.00 | 1 | $80.00
 | 4GB MicroSD Card | https://www.amazon.com/SanDisk-microSDHC-Memory-SDSDQ-004G-Packaging/dp/B00FM1JGHK/?th=1 | $8.49 | 1 | $8.49
 |  |  | $0.00 | 1 | $0.00
 |  |  | $0.00 | 1 | $0.00
 |  |  | $0.00 | 1 | $0.00
 |  |  | $0.00 | 1 | $0.00
 |  |  | $0.00 | 1 | $0.00
 |  |  |  | 1 | $0.00
 |  |  |  | 1 | $0.00
 |  |  |  |  | $0.00

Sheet: Sensors
Part number | Item description | Link | Cost per unit | Quantity | Total | Note | Total cost: | $9324.57
Canon XA15 | Camcorder |  | $1790.01 | 2 | $3580.02
 | Dummy battery for constantly powering camcorders |  |  | 2 | 0
 | Power supply for camcorder batteries |  |  | 1 | 0
Senal MC24-ES | Shotgun microphones for camcorders | https://www.bhphotovideo.com/c/product/1171345-REG/senal_mc24_es_professional_shotgun_microphone.html/mode/gsa | $149.95 | 2 | $299.90
Sennheiser MKE 500 | Shotgun microphone | https://www.bhphotovideo.com/c/product/878340-REG/Sennheiser_MKE_600_Shotgun.html (https://gcc02.safelinks.protection.outlook.com/?reserved=0) | $287.73 | 2 | $575.46
Infrared camera | Infrared camera |  |  | 1 | 0
Microsoft Azure |  |  |  | 1 | 0
Intel RealSense | RGBD camera | https://www.digikey.com/en/products/detail/82635DSD455/2311-82635DSD455-ND/12429610 | 423.75 | 2 | 847.5
AJA UTAP HDMI | HDMI to USB3 capture device | https://www.bhphotovideo.com/c/product/1248099-REG/aja_u_tap_hdmi_u_tap_usb_3_0_powered.html | 337.69 | 1 | 337.69
 |  |  |  |  | 0
Optitrack Trio | 3-camera motion capture system |  | $2999.99 | 1 | $2999.99 | Used for locating sensors in 6D space relative to the testbed table surface. Use of the Trio is enabled through the OptiTrack Motive software, available at https://optitrack.com/software/motive/.
 |  |  |  |  | 0
 |  |  |  |  | 0
HDMI Cables |  |  |  |  | 0
Laser pointers |  |  |  |  | 0
Laser pointer holders | 3D printed holder for the laser diode with extension cable |  | $4.00 | 3 | $12.00 | Custom 3D-printed part. Cost estimated.
Tascam MIXCAST 4 | Microphone equalizer and USB adapter | https://www.bhphotovideo.com/c/product/1623233-REG/tascam_mixcast_4_mixcast4_podcast_mixer.html (https://gcc02.safelinks.protection.outlook.com/?reserved=0) | $324.50 | 1 | $324.50
 | Light meter | https://www.bhphotovideo.com/c/product/1219219-REG/sekonic_401_474_litemaster_pro_l_478d_u_light.html (https://gcc02.safelinks.protection.outlook.com/?reserved=0) | $347.51 | 1 | $347.51
 | Sound meter |  |  | 1 | 0
 |  |  |  |  | 0
 |  |  |  |  | 0
 |  |  |  |  | 0
 |  |  |  |  | 0
 |  |  |  |  | 0
 |  |  |  |  | 0
 |  |  |  |  | 0
 |  |  |  |  | 0
 |  |  |  |  | 0
 |  |  |  |  | 0
 |  |  |  |  | 0

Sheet: Task boards
Part number | Item description | Link | Cost per unit | Quantity | Total | Note | Total cost: | 0

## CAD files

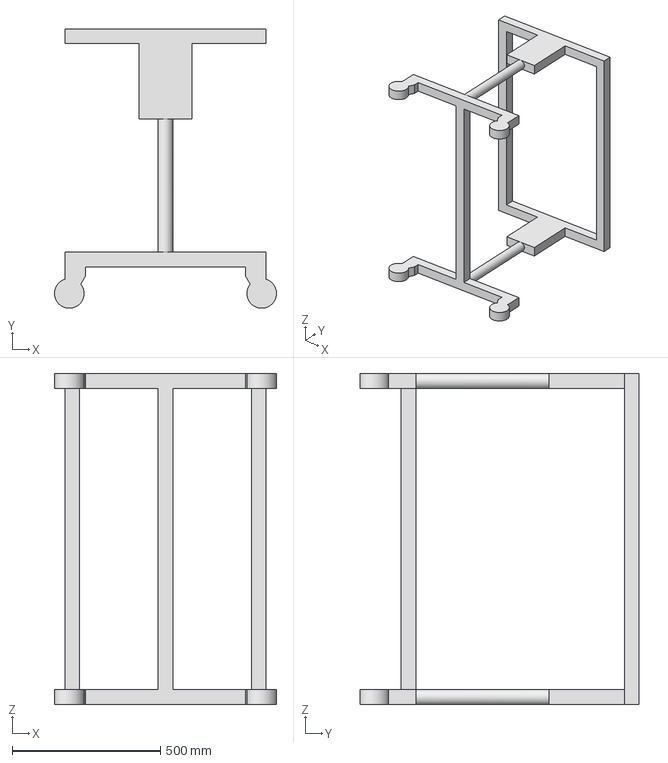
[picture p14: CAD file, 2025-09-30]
CAD Files/Testbed Components/Cart and Table Top/Human-Subject-Cart.step
750.0 x 944.0 x 1118.0 mm

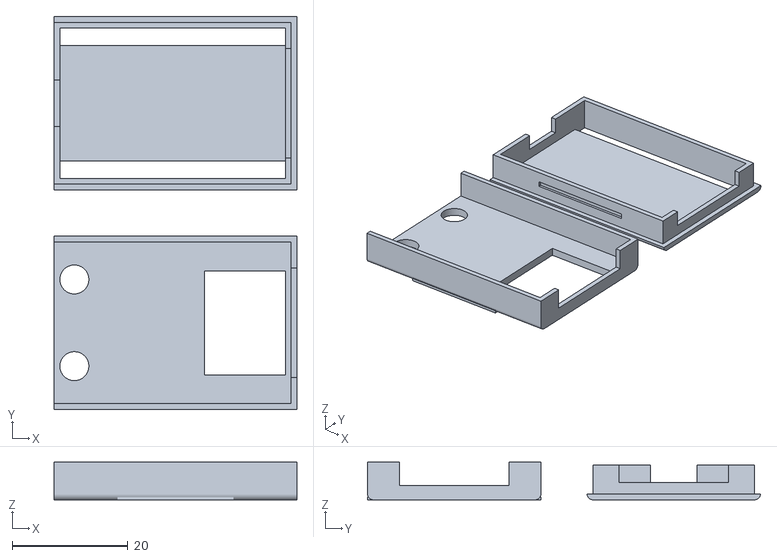
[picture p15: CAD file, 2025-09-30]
CAD Files/Testbed Components/ESP32/NIST - Espressif ESP32-C3-DevKitC Case.stl
42.0 x 68.0 x 6.50

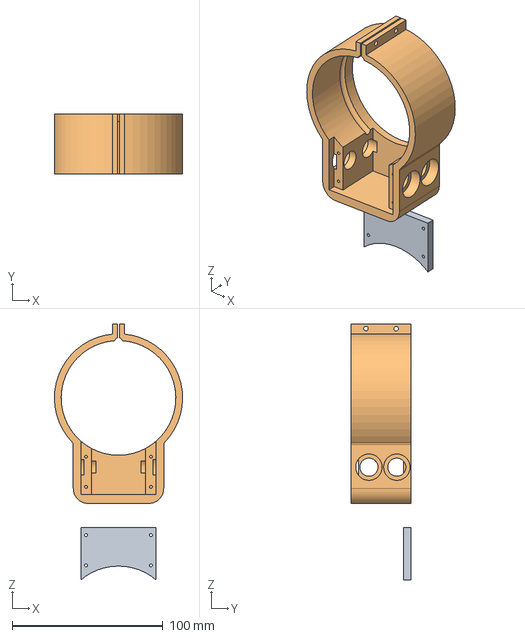
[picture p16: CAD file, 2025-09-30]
CAD Files/Testbed Components/Gripper Components/Robot_Button_Flange_V4.step
85.0 x 40.0 x 169.7 mm

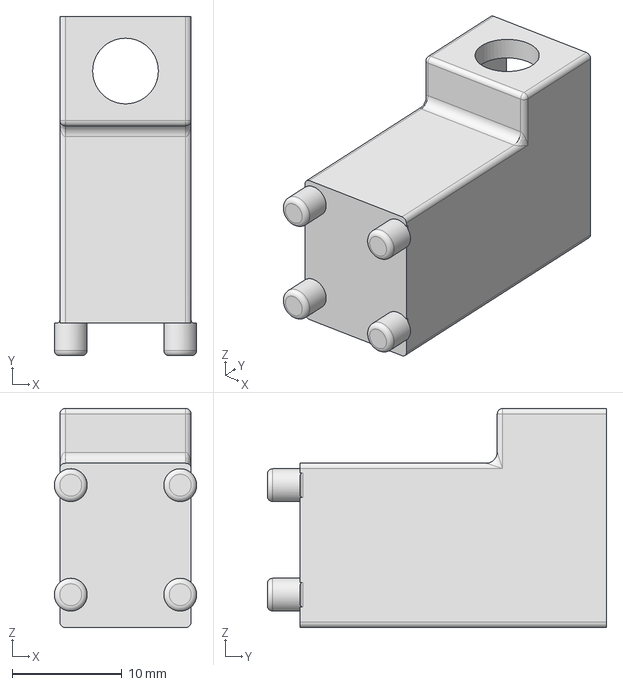
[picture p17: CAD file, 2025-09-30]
CAD Files/Testbed Components/Laser_Diode_Holder.step
13.0 x 31.0 x 20.0 mm

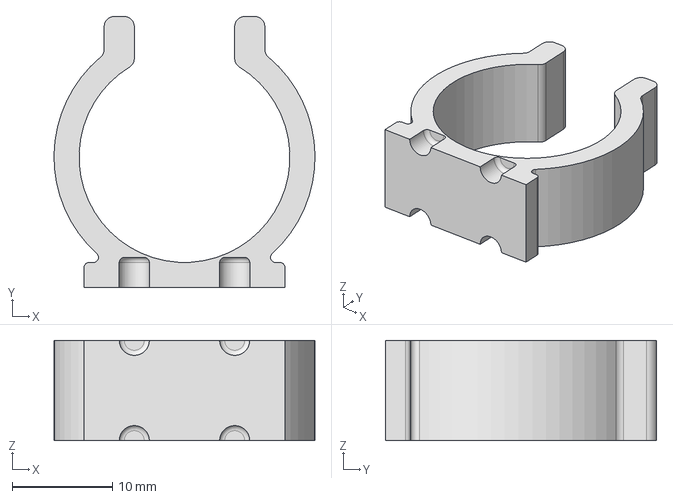
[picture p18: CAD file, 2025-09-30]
CAD Files/Testbed Components/MoCap Marker Plates/Clip Ring.step
26.0 x 27.0 x 10.0 mm

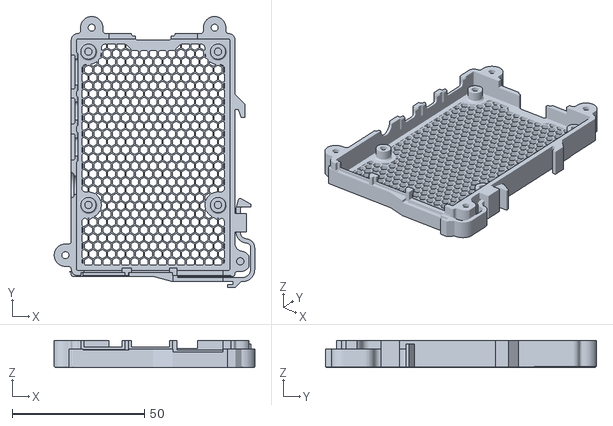
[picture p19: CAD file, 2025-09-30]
CAD Files/Testbed Components/Raspberry Pi/RPi 4B DIN Case Bottom.stl
75.9 x 102.5 x 10.3

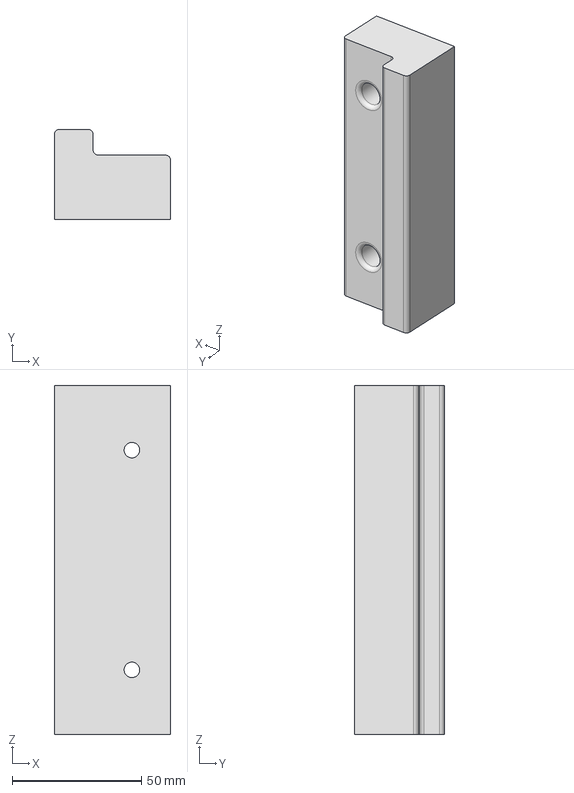
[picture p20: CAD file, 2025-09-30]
CAD Files/Testbed Components/Cart and Table Top/ForgeOSMount.step
45.0 x 35.0 x 135.0 mm

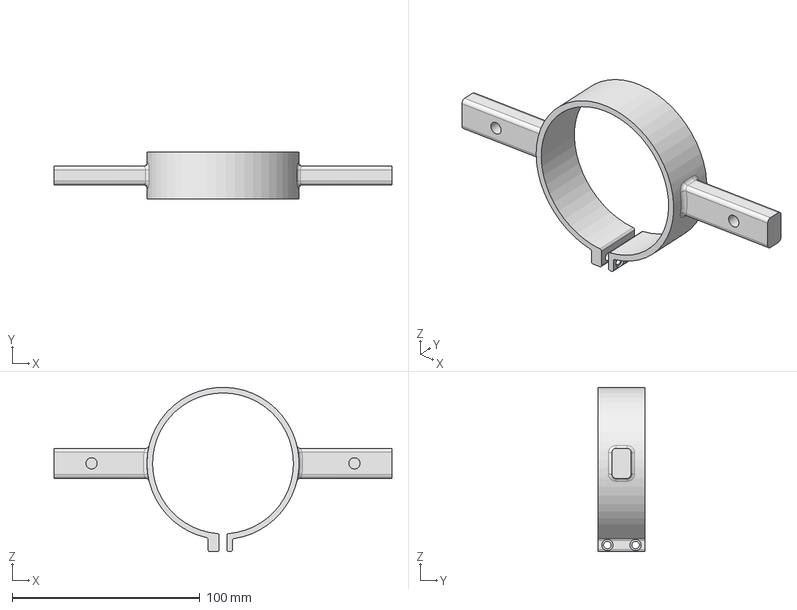
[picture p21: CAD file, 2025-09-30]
CAD Files/Testbed Components/Gripper Components/Robot_Button_Flange_V5.1_Flange.stp
180.0 x 25.0 x 87.5 mm

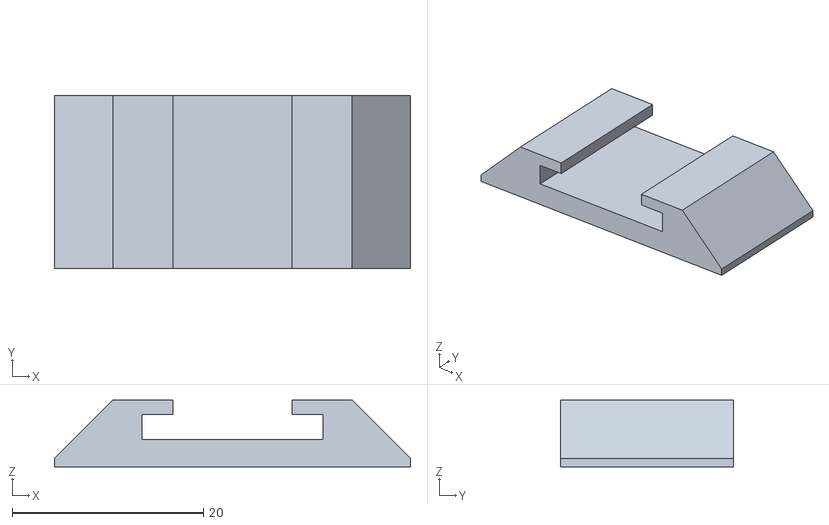
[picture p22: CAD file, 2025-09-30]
CAD Files/Testbed Components/MoCap Marker Plates/Cold Shoe Mount - Flat.stl
37.2 x 18.1 x 7.00

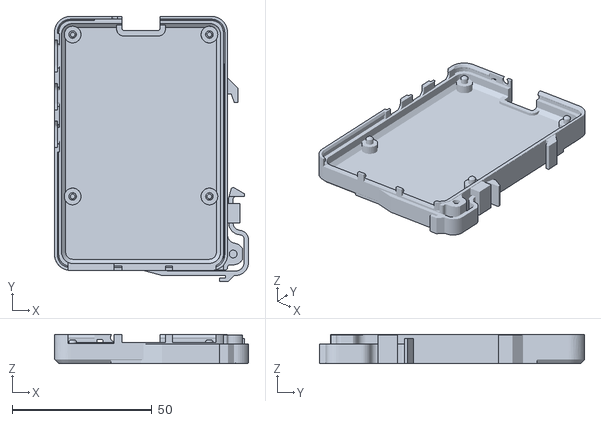
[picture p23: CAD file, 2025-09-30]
CAD Files/Testbed Components/Raspberry Pi/RPi 5 DIN Case Bottom.stl
69.5 x 95.0 x 10.5

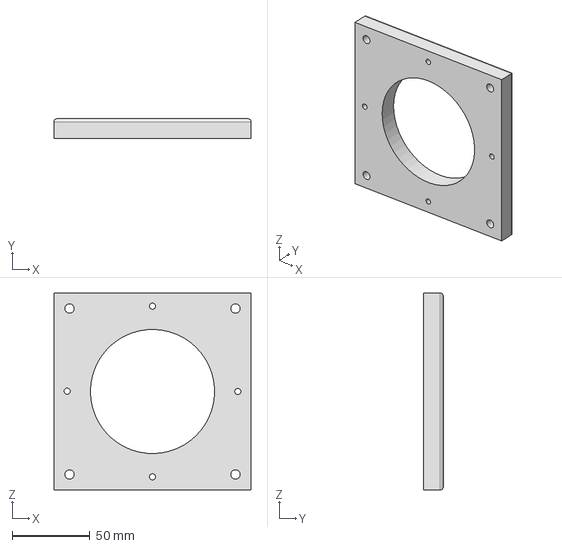
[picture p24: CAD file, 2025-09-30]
CAD Files/Testbed Components/Cart and Table Top/UR3 Mounting Plate.step
127.0 x 12.7 x 127.0 mm

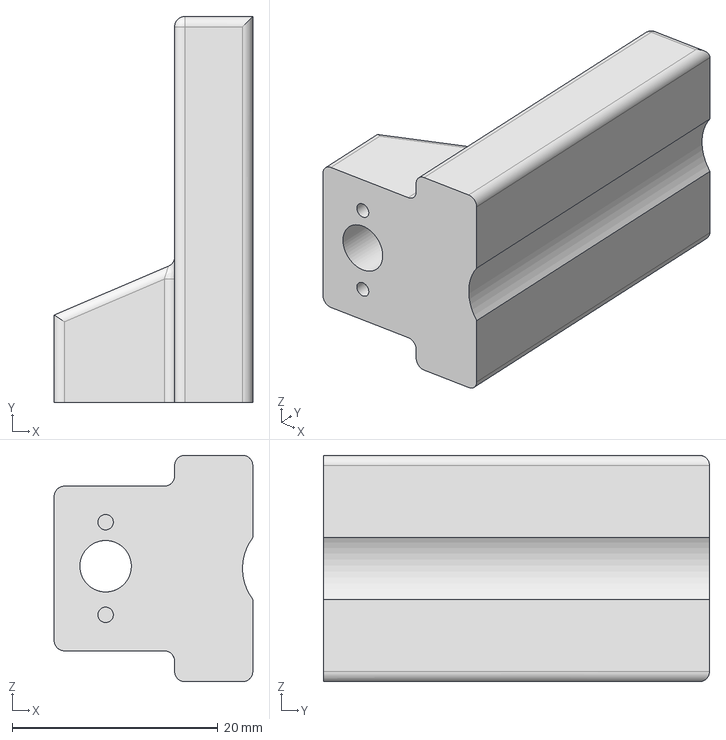
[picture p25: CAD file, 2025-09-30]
CAD Files/Testbed Components/Gripper Components/Robotiq_2Finger_Pad.step
19.3 x 37.5 x 22.0 mm

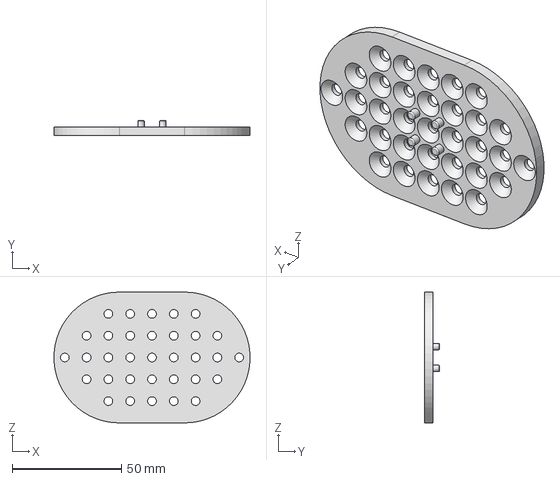
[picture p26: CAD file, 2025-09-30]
CAD Files/Testbed Components/MoCap Marker Plates/marker pattern.step
89.9 x 7.00 x 60.0 mm

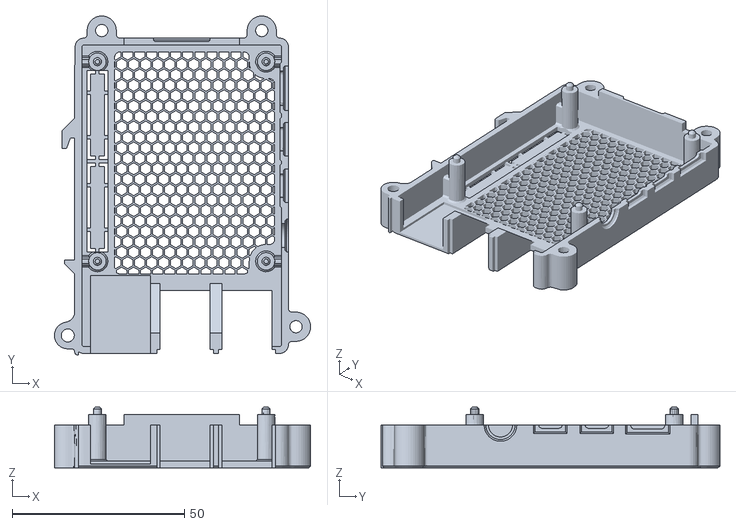
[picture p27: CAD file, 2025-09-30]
CAD Files/Testbed Components/Raspberry Pi/RPi 4B DIN Case Top.stl
74.4 x 98.5 x 17.7

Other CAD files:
CAD Files/Testbed Components/Cart and Table Top/Human Subject Testbed - Mounting Plate.step
CAD Files/Testbed Components/Gripper Components/Robot_Button_Flange_V4_FlangeOnly.obj
CAD Files/Testbed Components/MoCap Marker Plates/Cold Shoe Mount - Curved forward deep.stl
CAD Files/Testbed Components/Raspberry Pi/RPi 5 DIN Case Top.stl
CAD Files/Testbed Components/Cart and Table Top/Human Subject Testbed - Mounting Plate 2.stp
CAD Files/Testbed Components/Cart and Table Top/Human Subject Testbed - Mounting Plate.stl
CAD Files/Testbed Components/Cart and Table Top/Human-Subject-Cart.ipt
CAD Files/Testbed Components/Cart and Table Top/Human-Subject-Cart.obj
CAD Files/Testbed Components/Cart and Table Top/Human-Subject-Cart.stl
CAD Files/Testbed Components/Gripper Components/Robot_Button_Flange_V4.obj
CAD Files/Testbed Components/Gripper Components/Robot_Button_Flange_V5.1_Flange.stl
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

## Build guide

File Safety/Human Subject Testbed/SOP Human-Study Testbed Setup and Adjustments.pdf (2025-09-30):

# NIST Collaborative Robotics Testbed

Standard Operating Procedure: Human-Subject Testbed Setup and Adjustments

Version: 1.0
Last modified date: 3 October, 2024
Last modified author (name and contact email): Jeremy Marvel, jeremy.marvel@nist.gov

Change Log:
3 October, 2024
- First draft of the SSOP

### 1 Overview

This document outlines the safe standard operating procedures for the setup and modification to the human subject studies testbed for the collection of data for human-robot interaction research. This and related processes require the use of powered tools, some of which are considered hazardous to use. Operators of these tools shall be trained in their use. Training includes reading and demonstrating understanding of this document.

The standard operating procedures described in this document are provided to ensure the safety of activities involving constructing and modifying the human study testbed. This document is intended to serve as both training, and as a reference guide for the handling of materials and equipment. A copy of this document shall be kept present with the human study testbed for reference during setup and future modifications.

Access to the testbed and related components and tools is considered restricted to authorized personnel only.

### 2 Before You Begin: Safety

Be aware that the construction process includes the use of powered tools, which can cause injury if misused. Proper safety precautions shall be taken. The specific hazards associated with these tools and other related equipment are provided in the First Level Hazard Review (FLHR) repository (https://mmlweb.nist.gov/safety/).

The following FLHRs are specifically identified for the following actiities, and are not covered in this SOP:

Activity Name (ID) | Associated Activities | Link
Collaborative Robotics Research (735.13.0001) | Installing or modifying the testbed’s attached robot | https://mmlweb.nist.gov/safety/activities/10355
Collaborative Robotics Laboratory Laser Cutter (735.13.0059) | Using the laser cutter to create components for the testbed | https://mmlweb.nist.gov/safety/activities/6464
Material Machining Using a CNC Mill (735.13.0084) | Using the CNC mill to manufacture parts for the testbed | https://mmlweb.nist.gov/safety/activities/10328
Resin-Based 3D Printing (735.13.0096) | Using resin-based 3D printers to create parts for the testbed | https://mmlweb.nist.gov/safety/activities/9707
FDM-Style 3D Printing (735.13.0021) | Using filament-based 3D printers to create parts for the testbed | https://mmlweb.nist.gov/safety/activities/9992
2.1 | Tool Storage

All tools, when not in use, shall be stored in the appropriate tool chests to ensure easy location, access, and protection against accidental activation or contact with personnel. These tool chests include locks to prevent unauthorized access to tools with specific hazards (e.g., utility knives, drill bits, and power tools).

Locking tools in the tool chests to prevent unauthoried access/use is recommened, but not required, as additional activities in the laboratory may require their use.

2.2 | Eye Safety
2.2.1 | Material Contact with Eyes

Some tasks associated with this activity, such as cutting and drilling, may present hazards that could result in eye injury. The use of eye protection is required for personnel working on or near the human subject testbed during setup and maintenance. Eye protection includes the proper use of PPE such as safety glasses.

Proper PPE removal procedures shall be used.

Safety glasses shall be disposed of properly if damaged.

2.2.2 Laser Safety

Some tasks may involve the use of class 1 lasers for alignment and measurement purposes. Even though class 1 lasers are considered “eye safe,” care shall be taken to avoid accidental direct exposure of the eyes to the laser beams. Lasers shall be turned off while not in active use, and the use of safety glasses that include laser protection is strongly recommended.

Proper PPE removal procedures shall be used

Safety glasses shall be disposed of properly if damaged.

2.3 Hand/Skin Safety: Metal and Plastic Particulates and Shavings

Skin contact to materials removed from component parts of the testbed may result in small cuts, lacerations, punctures, or other injuries. The use of skin protection is strongly recommended when using drills or cutting tools so long as the use of PPE does not introduce new hazards (e.g., protective gloves and clothing may become engaged with cutting surfaces of power tools, resulting in significant injury). Skin protection includes the use of gloves (nitrile gloves are provided for general purpose use) and protective clothing (lab coats are provided for general purpose use).

Nitrile gloves shall be disposed of after use.

2.4 Respiratory Safety

Some tasks may generate particulates that may become airborne cause respiratory irritation. Dust masks are provided and required when drilling, cutting, grinding and sanding using powered tools.

Tasks involving lubricants, paints, or other chemicals shall be conducted in a well-ventilated area, preferably outdoors in fair weather. Aerosols, sprays, or related application mechanisms shall be used outdoors while wearing a provided dust mask.

Respirators are not required.

### 3 Activity: Drilling, Cutting, and Grinding

Always wear appropriate eye protection when using drills, cutting tools (hand saws, rotary tools, utility knives, etc.), and grinding tools (orbital sanders, rasps, rotary tools, sand paper, etc.).

3.1 Drilling:
1. Always keep hands and fingers away from the drill bit.
2. Properly secure all loose parts/components before attempting to drill materials.
3. Clean up any material waste by vacuuming any loose particulates from the floor and work surface.

3.2 Cutting:
1. Always cut away from yourself and others.
2. Properly secure all loose parts/components before attempting to cut materials.
3. Keep limbs and loose clothing away from the cutting surface.
4. Clean up any material waste by throwing large waste pieces into the trash, and vacuuming any
| loose particulates from the floor and work surface.
3.3 | Grinding:
1. Always remove material away from yourself and others.
2. Properly secure all loose parts/components before attempting to grind surfaces.
3. Keep limbs and loose clothing away from the grinding surface.
4. Do not use grinding tools near flammable materials, as metal parts may eject hot sparks that could
| ignite and create a fire hazard.
5. Clean up any material waste by vacuuming any loose particulates from the floor and work surface.

### 4 Activity: Manufacturing Component Parts

Refer to the appropriate FLHR(s) discussed in Section 2 for SOPs involving the laser cutter, CNC mill, and 3D printers. All other manufacturing procsses will be added to this section when they are identified and defined.

### 5 Activity: Moving/Removing Component Parts

When component parts are to be added to or removed from the testbed, the activity may involve handling parts that are heavy or sharp, and may therefore present pinching, cutting, or scraping hazards. Occasionally, cutting or striking tools may be required to separate parts from the testbed. During the removal process, nearby, unsecured parts may fall or be ejected from the testbed surface, presenting hazards to lower extremities. Always ensure a clean working surface around the source and destination of the parts being handled.

Specific equipment may require detailed instructions for proper handling when installing, moving, or removing. These details are provided in this section.

5.1 Robot: UR3e (mass: 11.2 kg ~17.7 lb; reach 500 mm)

1. The robot and its controller shall be disconnected from power sources (including electrical and
| pneumatic) before attempting to move. The robot shall be disconnected from the robot controller before attempting to move.
2. The robot shall be properly stored when not actively being used. Proper storage includes: 1) a
| mounting plate secured to a heavy and stable work surface, and 2) the original packaging in which the robot was shipped.
3. Before moving, ensure the proper storage solution is selected, installed correctly, and is free from
| nearby debris or obstructions. The travel path from the robot’s current location to its destination shall also be free from debris and obstructions.
4. It is recommended, but not required, that two people work together to move the robot to ensure
| proper management of connected components such as ancillary equipment, tooling, and cables/hoses.
5. If the robot is currently mounted to a plate, carefully remove the bolts securing the robot to the
| surface. The robot must be supported during this task, as it may be in an unstable configuration that could result in the robot falling when the securing bolts are removed. Supporting the robot can be done with a single hand given its low mass.
5.2 | Robot: Robotiq 2-finger adaptive gripper (0.925 kg)
1. The robotic gripper attaches to the tool flange of the robot using four retaining bolts. During
| installation and removal, use one hand to support the gripper while using the other to loosen and remove the bolts.
2. The robotic gripper has a rubberized signal cable that attaches to the robot arm’s tool-flange I/O
| port. The gripper came with a plastic gasket that goes over the I/O port of the robot arm, and prevents accidental contact with the signal cable during operation.
3. The robotic gripper may remain attached to the robot while moving the robot.
4. The stoc metal fingers have been replaced with 3D printed finger tips. If these finger tips break,
| carefully remove the retaining bolt from the finger tip and replace the damaged part with a new, undammaged finger tip.

### 6 Activity: Electronics Work

All work involving the construction or modification of electronic components shall be conducted at the electronics workbench at the end of the room. The electronics workbench has the appropriate tools and safety equipment to ensure personnel safety against risks of electric shock, and hazards associated with soldering processes.

When constructing or servicing electronic components, all power sources must be disconnected and/or discharged prior to working with the equipment to eliminate risk of electric shock. Personnel shall also use appropriate electrostatic discharge (ESD) equipment to prevent damage to electronic coponents.

Specific equipment may require detailed instructions for proper execution of electronics tasks. These details are provided in this section.

6.1 Soldering

1. Any activity involving melting solder (e.g., soldering components, or using a heat gun to reflow
| solder) requires the use of a desktop fume extractor. Fume extractors are already installed and powered at the electronics workbench.
2. The soldering irons in the human-robot interaction lab have adjustable heat settings. Set the
| soldering iron temperature to the lowest setting required to melt the solder.
3. To avoid burn hazards, use clamps or helping hands to hold parts being soldered, and allow the
| parts to cool for several minutes before attempting to handle with bare hands.
6.2 | Cutting, Stripping and Crimping Wire
1. Always use wire cutters to cut wire and cable. Do not use scissors or knives.
2. Always use wire strippers to remove the protective sheathing from wire and cables. Do not use a
| knife.
3. Always use a dedicated wire crimper to affix connectors, plugs, and attachments. Do not use
| pliers, tweezers, hemostats, or other grasping tools.

### 7 Activity: Laser Measurement and Alignment

Laser equipment may be used for measurement (e.g., distance measures) and alignment (e.g., laser pointers) purposes. Only class 1 (eye safe) laser equipment may be used during testbed setup and adjustment activities.

Laser-cutting shall be done in accordance with NIST FLHR 735.13.0059.

### 8 Activity: Moving the Testbed

When changing the location of the testbed within the human-robot interaction laboratory, loose objects may fall from testbed surface and become tripping hazards. The robot, controllers, and all ancillary equipment and sensors shall be rigidly affixed to the testbed.

9 | Emergency Response Plan
9.1 | Event: Fire

In the event of fire, immediately contact NIST Safety at x2222 to report the fire.

Authorized personnel may use an approved ABC fire extinguisher (combustible materials, flammable liquids, and flammable gases) to attempt to extinguish the fire. Acceptable fire extinguisher types include dry powder, alcohol-resistant foams, and carbon dioxide.

Do not use water to combat fires. Water may spread the flames.

9.2 | Material Hazards
9.2.1 | Event: Contact with Hot Tools or Parts

Cutting, drilling and grinding processes generate heat, and certain materials may retain a high temperature after cutting for several minutes. Should accidental contact occur, immediately check all impacted personnel for potential injuries such as cuts or burns, contacting NIST Safety at x2222 if there has been an injury.

9.2.2 Event: Tool Breaks or Loose Workpiece

Operations involving powered tools may result in cutting implements breaking or workpieces being forcibly ejected. If such events occur, recover any lost pieces of the damaged tools or parts and properly dispose of them; these pieces may have extremely sharp edges/points, so proper PPE is required when handling broken components.

Contact NIST Safety at x2222 if there has been an injury.

9.2.3 Event: Removed Material Contact with Skin or Eye

The removed material from the workpiece—and the workpiece, itself—are likely to have extremely sharp edges, and may result in skin or eye damage if contacted directly.

If contact with skin, immediately wash hands with warm water and soap and flush the affected region of skin with warm water. Do not brush or rub the affected region, as it may drive small slivers into the skin.

In contact with eye, immediately wash hands with warm water and soap. Flush eyes with gently-flowing water immediately for several minutes. Remove contact lenses, if present and easy to do.

DO NOT USE AN EYE WASH, as the high flow of water may cause chipped material to imbed in the eye and surrounding soft tissue. Seek medical attention to ensure that all material has been removed from the eye. This can be preformed by the NIST Health Unit during normal business hours.

9.2.4 Event: Removed Material Embedded in Skin or Eye

If removed materials are embedded in the skin, immediately wash hands with warm water and soap. Flush the affected region with warm water. Do not brush or rub the affected region, as it may further embed the material. If possible, gently remove the material from the skin.

If removed materials are embedded in the eye, immediately contact NIST Safety at x2222 and/or report to the Heath Unit in building 101. DO NOT TOUCH OR RUB EYE, OR ATTEMPT TO REMOVE THE OBJECT.

9.3 Chemical Hazards

This activity does not require the regular use of chemicals or materials with chemical hazards. However, some tasks may include the use of chemicals that present specific hazards.

9.3.1 Event: Chemical Contact with Eyes

Flush eyes immediately for several minutes using the eye wash station next to the fume hood or a sink in a nearby restroom. Remove contact lenses, if present and easy to do. Continue rinsing.

When possible, report to the Heath Unit in building 101 for a full evaluation.

9.3.2 Event: Chemical Contact with Skin

Remove any contaminated clothing immediately, and rinse skin in the closest restroom for several minutes.

When possible, report to the Heath Unit in building 101 for a full evaluation. Be prepared to describe chemicals used and their quantities/concentrations.

9.3.3 Event: Chemical Spill

In the event of a chemical spill, use the following steps to eliminate the hazard.

9.3.4 If the chemical agent is known

Always wear appropriate PPE.

Use the clean-up instructions specified in the agent’s SDS.

9.3.5 If the chemical agent is unknown

Always wear appropriate PPE.

Use the spill kit located to the left of the fume hood.

9.3.6 Event: Chemical Contact with Eyes

Flush eyes immediately for several minutes using the eye wash station next to the fume hood or a sink in a nearby restroom. Remove contact lenses, if present and easy to do. Continue rinsing.

When possible, report to the Heath Unit in building 101 for a full evaluation.

9.3.7 Event: Chemical Contact with Skin

Remove any contaminated clothing immediately, and rinse skin in the closest restroom for several minutes.

When possible, report to the Heath Unit in building 101 for a full evaluation. Be prepared to describe chemicals used and their quantities/concentrations.

9.3.8 Event: Inhalation of Chemical Vapors

The inhalation of chemical vapors may result in symptoms such as:
- Coughing,

- Shortness of breath,
- Eye/nose/throat irritation,
- Headache, and
- Dizziness.

If any of these symptoms manifest, immediately leave the laboratory and breathe fresh air. If others are in the laboratory, advise them to do the same.

When recovered, contact NIST Safety at x2222, and report the circumstances under which you were operating when the exposure occurred. Be prepared to describe the chemicals used and their quantities/concentrations.

When possible, report to the Heath Unit in building 101 for a full evaluation. Be prepared to describe chemicals used and their quantities/concentrations, and any symptoms experienced.

Do not return to the laboratory until breathing fresh air for a few hours, and having been given the all-clear by emergency personnel. Avoid closed spaces with poor air flow.

9.4 | Building Related Hazards
9.4.1 | Event: Fire

If a fire event occurs in the building and the building fire alarm sounds, immediately immediately turn off any powered equipment, place any tools/parts on the floor in a safe and stable position, and then evacuate the building per NIST guidelines for building evacuation

9.4.2 Event: Hazardous Weather

If a fire event occurs in the building and the building fire alarm sounds, immediately immediately turn off any powered equipment, place any tools/parts on the floor in a safe and stable position, and then move all personnel to the shelter-in-place zone in the building.

9.4.3 Event: Power Outage

Activate the E-stop button for any active robotic equipment, and turn off the power to the robot. If no emergency lighting source is activated, exit the room safely using a hand-held light source.

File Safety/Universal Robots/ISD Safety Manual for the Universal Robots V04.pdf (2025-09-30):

# ISD Safety Manual for the Universal Robots CB2, CB3, and E-series controlled robots

Prepared by:
Jeremy Marvel

National Institute of Standards and Technology 100 Bureau Drive, Mail Stop 8230 Gaithersburg, MD 20899-8230

Version History:
2014-08-05 | Original version
2016-02-01 | Updated for inclusion of the UR5 with the CB3 controller
2016-11-08 | Updated with new safety controller information
2024-12-09 | Updated format to more closely match other SOPs for the Human-Robot Interaction Lab
| Updated for inclusion of the e-series controller
| Updated for general UR safety rather than based on specific models
| Removed dual-arm configuration of UR10s
| Added information regarding non-collaborative use

Table of Contents

## 1 Overview

This safety manual outlines the standard operational procedures (SOP) and safety system features of the Intelligent System Division’s (ISD) collaborative robots, the UR3, UR5, and the UR10 from Universal Robots (UR). ISD owns and operates several UR model robots. These robots are lightweight enough that they can be trasnported and installed by hand, thus allowing for dynamic reconfigurability of the robotic testbeds. These robots use a number of different versions of the UR controller, each with its own capabilities and limitations. These are summarized below in Table 1.

Table 1. Universal Robots controller performance capabilities
Model | Power and Force Limiting | Force Measurement | Axis Limits | Safety Password | Initialization | Interfacing Ports
CB-2 | Yes (current monitoring) | Yes (current monitoring) | No | No | Large joint motions | Primary Client (30001) Fast feedback (30002) RT Client (30003)
CB-3 | Yes (current monitoring) | Yes (current monitoring) | Yes | Yes | Minimal joint motions | Primary Client (30001) Fast feedback (30002) RTDE (30004)
E-Series | Yes (current monitoring) | Yes (built-in force/torque sensor) | Yes | Yes | Minimal joint motions | Primary Client (30001) Fast feedback (30002) RTDE (30004)

The performance capabilities of the Universal Robots UR3, UR5 and UR10 are summarized in Table 2 below. The UR series was designed to pose a minimal hazard to users through power and force limiting by a combination of velocity limiting, mass reduction, and force/torque monitoring at the joint level.

Table 2. Universal Robots robot performance capabilities
| | UR3 | UR5 | UR10
Number of axes | | 6 | 6 | 6
Maximum reach | | 500 mm | 850 mm | 1300 mm
Repeatability | | ±0.1 mm | ±0.1 mm | ±0.1 mm
Mass | | 11 kg | 18.4 kg | 28.9 kg
Axis capabilities | Joint | Range | Velocity | Range | Velocity | Range | Velocity
| 1 | ±360° | 180 °/s | ±360° | 180 °/s | ±360° | 180 °/s
| 2 | ±360° | 180 °/s | ±360° | 180 °/s | ±360° | 180 °/s
| 3 | ±360° | 180 °/s | ±360° | 180 °/s | ±360° | 180 °/s
| 4 | ±360° | 360 °/s | ±360° | 180 °/s | ±360° | 180 °/s
| 5 | ±360° | 360 °/s | ±360° | 180 °/s | ±360° | 180 °/s
| 6 | Infinite | 360 °/s | ±360° | 180 °/s | ±360° | 180 °/s
Rated Payload | | 3 kg | | 5 kg | | 10 kg
Max Cartesian speed | | 1000 mm/s | | 1000 mm/s | | 1000 mm/s
Mounting flange | | DIN ISO 9409-1-A50 | | DIN ISO 9409-1-A50 | | DIN ISO 9409-1-A50

UR robots fall under the classification of “industrial robots,” and are thus subject to the safety requirements outlined in ANSI/A3 R15.06:2012. Per these standards, industrial robots are considered “incomplete machines,” and require the addition of ancillary equipment such as end-of-arm tools (such a grippers or welding tips), safeguards, and application-specific machinery. This ancillary equipment may introduce additional hazards to the robot’s application, and shall be assessed separately in the SOP for the application.

Safe usage of the robots relies on the following:
- Trained operators who follow safe procedures
- Demonstrated understanding of the robot’s functionality and work volume
- Universal Robots’ integrated safeguards verified by operators to work correctly
- ISD added engineering and administrative controls verified by operators to work correctly

The engineering and administrative controls are the result of a task and risk analysis conducted on a range of anticipated scenarios involving the use of UR robots, but does not specify the actual operating procedures of the applications, themselves. Any application involving UR robots shall be accompanied by a purpose-written SOP for that application. That application’s SOP shall follow NIST and EL hazard policies and the procedure described in ANSI/A3 R15.06:2012 Industrial Robots and Robot Systems – Safety Requirements. Please contact the authors of this document when installing new equipment in the workcell and/or running new programs using the robots’ controller or any external controllers.

## 2 Before You Begin: Safety

The use of the Universal Robots robotic platforms includes the utility of industrial robotic manipulators and attached tooling, which can cause injury if misused. Proper safety precautions shall be taken. The specific hazards associated with these tools and other related equipment are provided in the First Level Hazard Review (FLHR) repository (https://mmlweb.nist.gov/safety/).

### 2.1 Industrial Robots

Each robot consists of a controller and an actuated manipulator. Both the controller and the manipulator present hazards that can cause severe injury when misused. By itself, the robot does not actually do anything. It must be integrated into a robotic system, which consists of:
1) the robot,
2) end-of-arm tooling for part manipulation or processing,
3) the environment in which the robot is installed,
4) any ancillary equipment (e.g., tables, conveyors, fixtures, and machines including other robots) required to complete the task,
5) the parts being worked on, and
6) safety equipment including safeguards, barriers, sensors, and safety controllers.

Unless collaborative functionality is specifically identified as being required in the application’s standard operating procedure, the use of the UR robots shall be assumed to be limited to non-collaborative applications.

Robot users shall familiarize themselves with these risks and safeguards, and are responsible for obtaining specified training from the people responsible for division safety and robot operation. Robot users should read the relevant robot safety handbooks, and should also notify the responsible personnel of potential risks and hazards identified or encountered during robot use.

### 2.1.1 Non-Collaborative Applications

By default, the robots shall be assumed to be used in a non-collaborative application. Non-collaborative applications assume specific hazards exist that will present safety risks to people in or around the application.

In non-collaborative applications, efforts shall be taken to prevent access of people to the robot’s work volume. Such efforts include the use of physical barriers and sensor-based safeguards that will issue an emergency stop to the robotic equipment if a person is too close. Any safeguards used shall be verified such that access to the active robot’s work volume is prevented.

### 2.1.2 Collaborative Applications

Collaborative applications are those that expect robots to operate in automatic mode in the vicinity of people without physical barriers. This vicinity may necessitate the close proximity people to the robots such that the robot and people can occupy the same working volume, and, in some applications, may necessitate the physical contact between robots and people.

In applications in which UR robots are used collaboratively, specific details shall be provided to justify the necessity for collaborative functionality. Specifically, physical proximity/contact shall be warranted, and details regarding why the use of non-collaborative functionality could not be used instead.

Collaborative applications may involve sub-tasks that are non-collaborative in nature. During these sub-tasks, access to the robot and its work volume shall be restricted.

To be permitted to be used in collaborative applications, the following must be present, fully documented in the application SOP, and shown to be properly filling their intended function:

1) collaborative safety functions to prevent injury,
2) safeguards to prevent unauthorized access to non-collaborative aspects of the robot application,
3) all equipment used in/around the collaborative workspace has been designed for collaborative applications (including rounded edges, reduced speeds and mass, and coverings to prevent access to pinching/rubbing/cutting/sheering hazards,
4) test methods and metrics for verifying and validating the safe installation and use of the robotic system, and
5) demonstrations of functional safety.

### 2.2 Eye Safety

The UR robot does not present any specific hazard to the operator’s eyes. However, the robot application may involve handling, manipulating, or working on parts that could introduce hazards that could affect the operator’s eyes.

In general, the operator shall keep their head outside of the robot’s work volume. Otherwise, the operator risks injury to the face and eyes that can result in injury or blindness.

If close proximity to the operator’s face is required (e.g., inspecting power connections, or doing precision work within the work volume), the operator shall wear safety glasses with side shields to prevent accidental contact with the face and eyes.

If used, safety glasses shall be disposed of properly if damaged. Safety glasses must be maintained by regular cleaning and disinfecting, and regularly inspected for damage. Scratches, clouding, or other damage to the lenses could impair vision, introducing a new hazard to the operator.

### 2.3 Hand/Skin Safety

The moving parts of the robot manipulator can introduce physical hazards to the operator’s skin on the hands and arms.

Pinching and crushing can occur at the robot’s joints, and between the physical parts of the robot and immovable parts of its environments (e.g., between the robot’s tool flange and the surface of the table on which the robot is mounted).

Impacts between the robot and the operator may result in bruising, cuts, punctures, or broken bones, especially when the robot manipulator is moving at maximum velocity.

Abrasions and cuts on the extremities may also occur if the robot moves across the operator’s skin.

Additionally, with extended use the robot manipulator and controller may become hot, posing a burning hazard.

In general, the operator should keep hands, arms, and other parts of their body away from the moving parts of the robot. Maintaining a safe operating distance from the robot will prevent accidental contact, and any hazards associate with that contact.

It is recommended the operator wear long sleeves when working near/with the robot to reduce the risk of injury. Gloves are not recommended as they may become hooked on the equipment and create new hazards to the hands and fingers.

### 2.4 Common Hazards

The following is a list of common risks and the controls, training, and/or Personal Protective Equipment (PPE) necessary for reducing each risk:

1) Operator using teach pendant to jog or run a program on the robot causes robot to strike themself or someone else.
Engineering Controls
a. Robot has integrated collision detection that stops the motions of the manipulator when unexpected impacts occur, even while training the robot
Training
a. Train users to maintain distance from the robot when possible; avoid pinch points, etc. to reduce the probability and severity of impacts
b. Train users to ensure that multiple people are not allowed inside the robot workzone unless they are working on a common task
2) Personnel struck by robot while robot is operating in automatic mode
Engineering Controls
a. Robot has integrated collision detection that stops the motions of the manipulator when unexpected impacts occur
b. Integrated safety controller has connections for external safeguards to monitor and protect non-collaborative zones
Training
a. Train users that red warning light indicates robot arm power is on and that the robot can begin moving at any time to reduce the probability of an impact
b. Train users to ensure that multiple people are not allowed inside the robot workzone unless they are working on a common task
c. Operators must have a hand on or near an e-stop while the robot is active
d. Collaborator must have easy access to an e-stop during collaborative robot scenarios
3) Working on equipment attached to the robot when the arm power is turned on and the robot is in automatic mode could cause the robot to strike someone
Training
a. Train users to ensure that the work volume is clear before turning on the robot controller to reduce the probability of impact
b. Red warning light indicates to users that the robot drives are enabled and that they should stay clear of the robot work volume to reduce the probability of impact
4) Working on robot electronics or mechanical components when robot controller is turned on and the robot is in automatic mode could cause the robot to strike someone
Training
a. Train users to unplug the robot power – eliminates probability of impact.

### 2.5 Required PPE

Use of the UR robots does not require any specific PPE other than that which has already been mentioned, though the application in which the robots are used may require the use of PPE.

Any PPE required by the application SOP shall be stored near the equipment in a location that provides easy access to the PPE without presenting any risks to the person.

## 3 Robot Safety Controls

The following section is a brief overview of the engineering controls of UR robots.

Refer to the Universal Robots documentation for a more detailed description of the safety features of the robot and its controller, and to the appropriate manuals and specifications of individual sensor packages for the robot workcell. Each document is available online with the associated First Level Hazard Review, and can also be found in a documents folder accompanying the testbed.

### 3.1 Integrated Robot Safeguards

The following safeguards are built into the UR controller and manipulator.

These safeguards provide safety for the robot only, and are insufficient to provide functional safety of the robotic system and the associated robot application.

Additional safeguards and safety functions are required to ensure the safety of the robotic application.

### 3.1.1 Emergency Stop

Universal Robots provides a single emergency stop (E-Stop) button on the teach pendant (see Fig. 1). The E-Stop button causes the robot to stop immediately. Along with an observant operator, it provides an important component to the safety system.

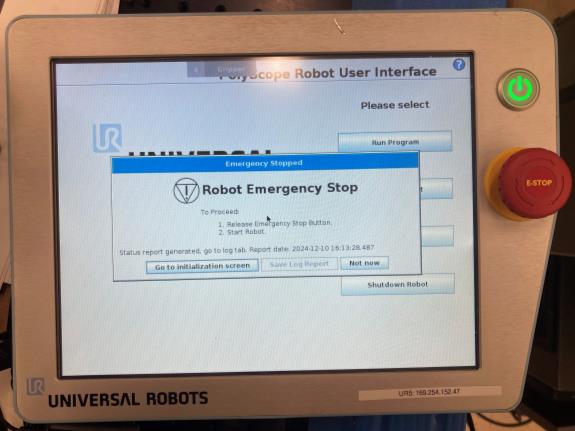
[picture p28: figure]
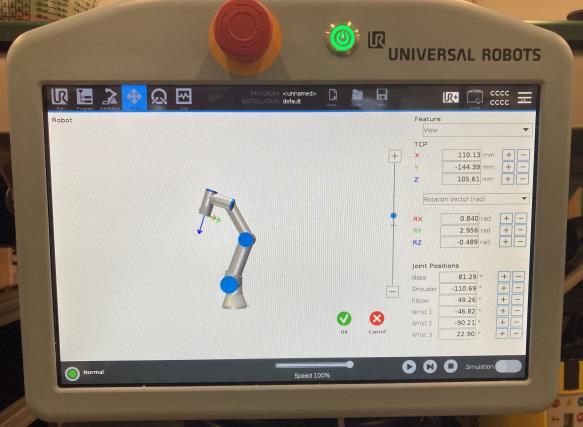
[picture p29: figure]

Figure 1: The front of the teach pendant for the CB (left) and E-Series (right) controllers. The emergency stop is the large mushroom button on the left and top of the CB and E-Series pendants, respectively.

### 3.1.2 Mechanical Hard Stops

Only joint 6 on the UR3 has infinite rotational capabilities. All other joints on the UR3, and every joint of the UR5 and UR10 are limited in rotational range by mechanical hard stops to prevent damage to the robot’s drives. These hard stops physically prevent the robot from moving beyond a set point.

### 3.1.3 Soft Axis Limit Switches

The Universal Robots robot system imposes adjustable software-defined limits on the ranges of the axes, and automatically stops the robot if any of these ranges are exceeded. These limit switches are always enabled, but are principally used for machine protection (they are adjusted such that the robot cannot hit the mechanical end stops) and can be edited by the operator to modify the active work volume of the robot.

The UR CB3 and E-Series controllers have the option of setting Cartesian axis limits to prevent the robot from moving beyond certain points in the environment as an added protective measure. These Cartesian limits apply only to the robot’s end effector, however, and it is possible to drive other parts of the robot beyond these limits.

The UR CB2 controller does not have Cartesian axis limiting.

### 3.1.4 Collision Detection

The Universal Robots controller monitors joint currents and torques at all times, halting the robot on over-current or over-torque events. Collision detection is always running while the robot is powered on, and will halt the robot if it measures that it has encountered forces in excess of 150 N, causing the robot to issue a safeguard stop.

This value may be adjusted on the controller to be more or less sensitive (i.e., triggering at lower forces). Collision detection may be inadvertently tripped if the robot is carrying an object that is heavier than expected. The object’s mass must be indicated in the tool description to prevent unintended behaviors.

Collision detection has been known to not be 100% reliable.

It has been observed that while the robot is accelerating quickly to high velocities, the currents necessary to accelerate the robot may be comparatively large. Impacts that occur while the robot is accelerating are not always detected, and may result in contact forces in excess of 600 N. While this prominently impacts older models of robots, as a best practice is it advised to use reduced speeds and lower accelerations.

Current monitoring may also be negatively impacted by power fluctuations. It is recommended the UR robots not be powered by a battery-fed DC-AC inverter, as low battery charge may result in inconsistent or unpredictable power to the robot controller.

### 3.1.5 Safety Input/Output Signals

Universal Robots provides the following safety interfaces on their controllers:
1. Safeguard channels A and B – control signal to the UR controllers in automatic mode.
a. Decelerates the robot and limits arm power
b. Pauses robot program being executed
c. Must be reset manually (this requires operator to acknowledge the error, re-enable the arm, and restart the program)
2. External E-Stop channels A and B – control signals to the UR controllers for external emergency stop devices
a. Emergency stops robot:
i. Issues stop category 0
ii. Generates an error that must be acknowledged
b. Must be reset manually (this requires operator to acknowledge the error, re-enable the arm, and restart the program)

These connectors are located inside the controller, and are located on the far left of the array of terminal connectors (see Fig. 3).

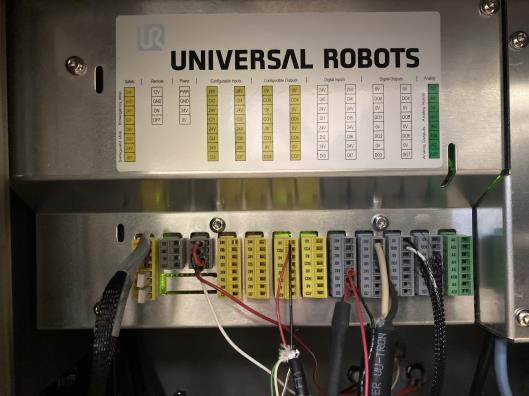
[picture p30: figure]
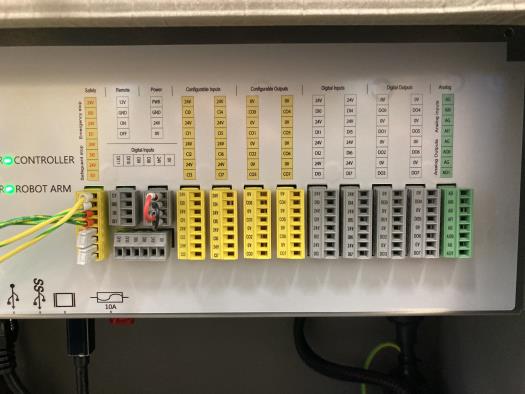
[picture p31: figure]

Figure 3: The safety signal connections of the teach pendant for the CB (left) and E-Series (right) controllers.

Each safety signal consists of two channels, A and B, which includes a source and a sync. Each channel’s sync must be connected to its respective source (e.g., the source for safeguard channel A is connected to the sync for safeguard channel A), and both channels must be fully connected for operation to be possible

### 3.1.6 Electronic Safety Circuit

The UR controllers maintain dual-channel safety system that constantly monitors all connected safety-relevant components and devices. In the event of a fault or interruption in the safety circuit, power to the robot’s drives is removed and the program is paused. A notification window will be displayed in the event of a safeguard event. When the safeguard event is cleared, the current program and the robot’s motions will automatically resume.

### 3.1.7 Safety Rated Stopping Functions

Table 3. Stopping functionality of the UR robots based on the operational mode and halting trigger.
Trigger | Result
Safeguard | STOP2
E-Stop pressed | STOP0
Encoder error | STOP0
Controller turned off / power failure | STOP0

The different stopping reactions of the robot system are triggered in response to different monitored events or as a reaction to operator action. The UR controllers may issue a stop category 0 (STOP0, robot is stopped immediately when the brakes are applied, the current program is stopped, and power to the drive is removed) or category 2 (STOP2, robot is stopped with a normal braking ramp, the brakes are not applied, and the drive are not deactivated) according to DIN EN 60204-1:2006 based on safeguard triggers. The stopping characteristics according to the operational mode and trigger are summarized in Table 3.

### 3.2 External Safeguards

Using the safety channels discussed previously, additional external safeties may be integrated into the robot’s controllers, either directly, through a safety PLC, or a custom safety circuit. These are not provided by UR, and must be integrated by NIST personnel.

The types, number, location, and integration method may change according to the needs of the robot application.

This section discusses safeguards, sensors, and signals that are recommended for the integrated robot system for the robot application. These are not the only safeguards that can be used, but reflect only those safeguards that have been used by the authors of this SOP.

### 3.2.1 Emergency Stops

Of all possible safeguards that can be integrated, the only ones that MUST be added are external emergency stops.

At least one external E-Stop button stop shall be integrated into the testbed. Any number of E-Stop buttons can be daisy chained serially to ensure that any actuation of an E-Stop button results in the entire circuit signalling a category 0 stop.

E-Stop buttons shall be positioned such that at least two people can actuate a stop action independently of each other outside of the robot’s work volume. Only safety-rated E-Stop switches (e.g., see Fig. 4) are permitted for use as E-Stop buttons.

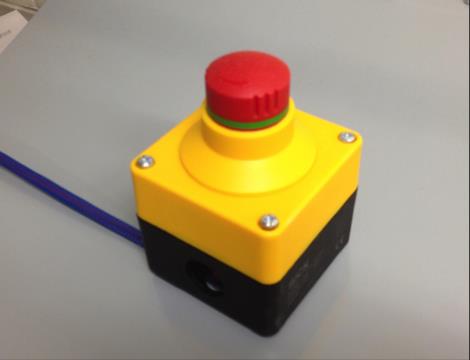
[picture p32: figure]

Figure 4: E-Stop buttons (yellow boxes) can be integrated into the robot testbed through the safety controller.

### 3.2.2 Light Tower

A single light tower indicates the functional state for a single robot in the robot testbed. Applications leveraging multiple robots should have separate light towers for each robot to indicate their individual states. Light towers shall be rigidly installed such that they are visible from all angles of approach, and may be integrated either vertically or horizontally. Separate indicator lights may also be used provided they are linearly arranged such that their functionality and relation to each other remains clear (e.g., see Fig. 5).

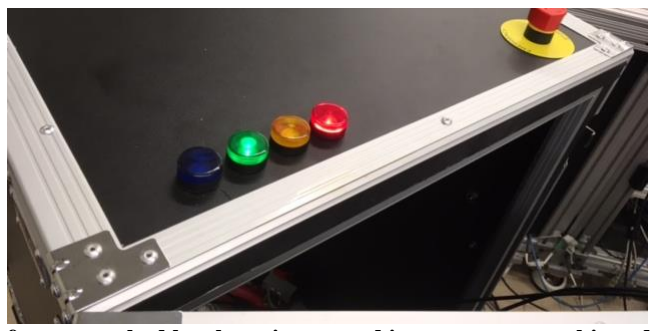
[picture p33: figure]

Figure 5: The light tower for one testbed has been integrated into a separate cabinet designed for transportation and storage of the robot.

Audible warnings are not required for use to alert the operator of changes in robot state.

Table 3 indicates the messaging and order conventions adopted by ISD’s PHRI laboratory. In summary, the critical elements to be conveyed include: the state of the robot’s drives, possible error state(s) of the robot, and whether or not safeguards are functioning correctly. Some tasks may involve the use of muting safeguards, in which case such states shall also be indicated.

Table 3. ISD Universal Robots testbed light tower function.
Light Color | Function
RED | When lit, the RED light indicates that the robot’s drives have been energized. The robot may move without warning, so all personnel should treat the robot as though it was active.
AMBER | When lit, the AMBER light indicates a safety signal has been triggered and the robot is in a safeguard fault state. If the RED light is also illuminated, the robot may start moving as soon as the safeguard signal is cleared.
GREEN | When lit, the GREEN light indicates that powered safeguards (e.g., laser scanners or light curtains) and safety systems are active and are functioning as expected. The functionality of unpowered safeguards (e.g., safety mats, enabling devices, etc.) are not indicated by the GREEN light unless integrated into a powered safety system.
BLUE | When lit, the BLUE light indicates one or more safeguards have been muted, allowing the robot to move even under conditions that would normally cause it to stop/pause. If the BLUE light is lit, all personnel should assume that the safeguards are being ignored.

### 3.2.3 Laser Area Scanners

Laser-based, safety-rated area scanners detects objects around the robot testbed in both protected and warning zones. Protected zones cover the area immediately surrounding the robot’s working volume. When a scanner detects an undefined object, the scanner activates the safeguard signal, stopping the robot if it is in automatic mode unless its signal is muted.

Warning zones cover the areas leading up to the protected zone and 3000 mm from the center of the sensor. Beyond 3000 mm, the area scanner’s ability to detect smaller objects (e.g., the cross-section of a leg) is diminished due to the spread of adjacent detection beams. When the scanner detects an object within the warning zone, a signal is sent through a connected safety system, but does not require the robot to stop.

### 3.2.4 Pressure-sensitive Mats

A safety-rated, pressure-sensitive mat may be placed on the ground just outside of the robot’s work volume. This mat would tie into the safeguard circuit, and triggers a sensor-based safeguard stop when someone or something applies pressure.

### 3.2.5 Enabling Devices

Three-position enabling devices may be integrated into the system as operational mode switches into the C12 and C13 inputs on the safety signal connection (each with a respective, separate 24V output located above the input). By default, both the CB and E-Series controllers support only a single external enabling device to be added. Additional enabling devices can be added by means of a custom safety circuit.

## 4 Powering and Initializing the Robot

One or more personnel are required to be on station when operating the robot. While the drives are enabled, at least one person must be manning an E-Stop button. Whenever an operator is working inside the safeguarded space, that operator must have an enabling device, a teach pendant, or an E-Stop device.

Prior to turning on power, visually verify the following:

1. Mechanical mounting of robot to platform, verifying that the robot is firmly attached and stable.
2. All electrical connections are secure.
3. All applicable utility connections (e.g., air, communications, or auxiliary sensor and control cables) are secure.
4. All peripheral equipment and systems are stable and out of the way.

The operator shall perform the following steps when turning the robot power on:

1. Verify that the robot is ready, including verifying that cables and components are secure.
2. Verify that no one is inside the robot workzone. If so, then the operator shall notify persons inside the workzone that the arm power is going on.

NOTE: While the robot is initialized, the drives are active and the robot is awaiting motion commands. Such commands may be sent remotely, so it should be assumed the robot might move without warning. When the robot is not in use, disable it by pressing the “OFF” button on the Initialization screen on the teach pendant, or by pressing one of the E-Stop buttons.

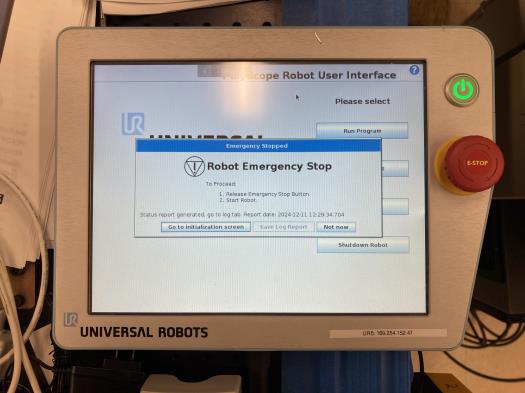
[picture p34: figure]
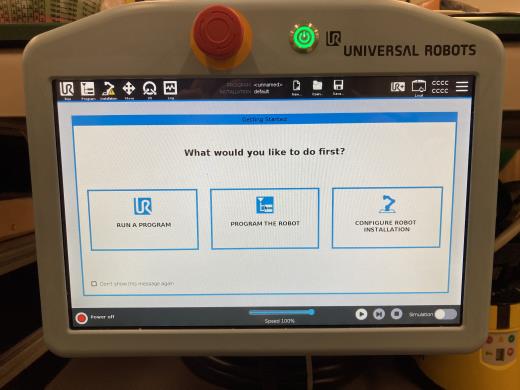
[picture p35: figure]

Figure 6: The front of the teach pendant. The robot is turned on by pressing the silver power button at the top-right corner of the CB teach pendant, or in the top center of the E-Series teach pendant.

### 4.1 Turning on the Robot

1. Press the power button on the teach pendant (see Fig. 6). This will turn on the controller, which supplies the robot with power.
2. Allow the robot to boot normally.
3. On the CB teach pendant: You will be presented with a prompt stating that the robot has changed modes (CB2) or is in an emergency stop state (CB3), and will then be instructed to go to the initialization screen. Using your finger, press the “Go to initialization screen” button.
4. On the E-Series teach pendant: You will be shown the default “What would you like to do first?” screen. Using your finger, press the red button on the lower left corner of the screen. Once the startup is complete, the user will be prompted to initialize the drives.

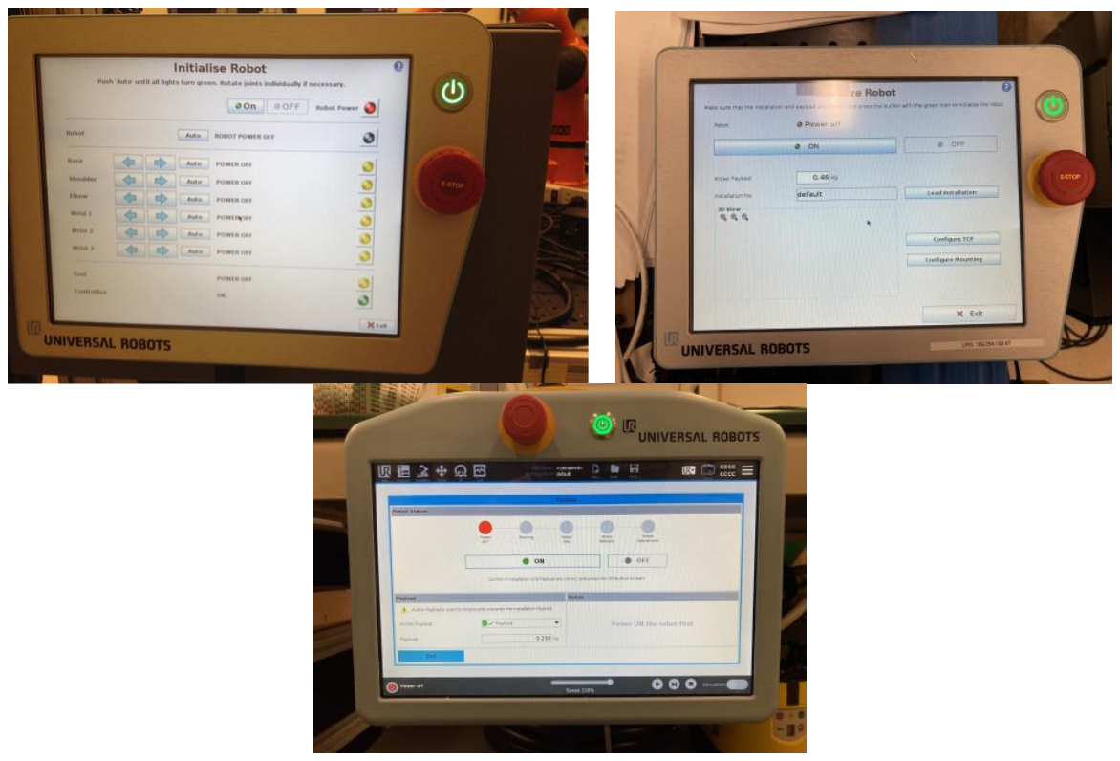
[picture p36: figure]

Figure 7: On the initialization screen the user will be presented with options to turn on and off the robot. Depending on the version of the controller, this screen will have a different appearance. The CB2 controller (top left) will show the states of all joints, while the CB3 (top right) and E-Series (bottom) controllers will not.

### 4.2 Initializing the Robot

CAUTION: RISK OF STRUCK-BY AND PINCHING/CRUSHING HAZARDS

Initializing the robot does not require the operator to be inside the robot’s work volume. The CB2 controller requires large motions of the robot to initialize the encoders, while the CB3 and E-Series controllers require only minimal motions. All personnel shall be outside the robot’s work volume while initializing the robot.

1. With your finger, press the “On” button at the top of the screen. This will boot the drive amplifiers and energize the robot’s joint motors, but will not release the brakes.
2. Wait for the drives to boot.(the status next to each entry on the joint list will say “ready” once this is complete). Continuing beyond this point, the robot will move to measure and validate its joint motor encoders. The area around the robot shall be clear of obstacles and personnel.
3. Press the “Start” button on the teach pendant screen. The brakes will release and the robot will begin to move.
a. On the CB2 teach pendant: Press and hold the “Auto” button while the joints calibrate. Each of the joints will begin moving from their current configuration.
i. If the robot looks like it will collide with its environment or itself, release the “Auto” button and then press and hold it again. This will reverse the direction of motion for any joints that have not yet been calibrated. Once an individual joint has been calibrated, it will automatically stop moving.
ii. To manually initialize the joints, use the left and right arrow keys on the teach pendant to move each joint individually.
iii. The status for each joint will change from “Initializing” to “OK” as they are calibrated, and the status indicator at the right of the screen will change from yellow to green.

b. On the CB3 and E-Series teach pendant: All of the robot’s joints will move slightly from their current configuration, but the range of motion will be small to prevent unnecessary risk.
4. At this point the robot is powered, initialized, and is ready to move. While the robot will not move unless running a program or being manually jogged, all personnel around the robot shall be aware that it is now possible the robot can move at any time and in any direction without any advanced warning. Close the intialization screen to return to the main menu.

### 4.3 Moving the Robot

CAUTION: RISK OF STRUCK-BY AND PINCHING/CRUSHING HAZARDS

Moving the robot may result in parts of the body or objects in the environment being struck, pinched, or crushed by the robot and/or its tooling. This applies to all modes of moving the robot, including jogging the robot using the move screen, Freedrive mode, or while the robot is running a program. Keep limbs away from pinch points (e.g., between adjacent links at the robot’s joints, or between any part of the robot and rigidly-mounted parts of the environment) while moving the robot. Keep head and face away from the robot. Apply an E-Stop when not actively using the robot.

Once initialized, the robot can be moved under its own power. The UR robots do not have separate “teach” and “automatic” modes, and an enabling switch is not required to jog the robot.

### 4.3.1 Commanding Motions Using the Move Screen

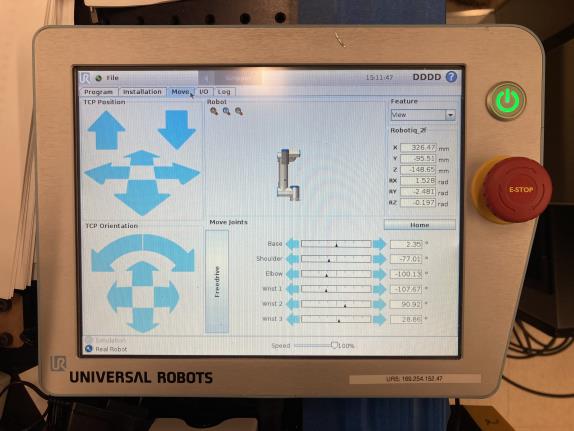
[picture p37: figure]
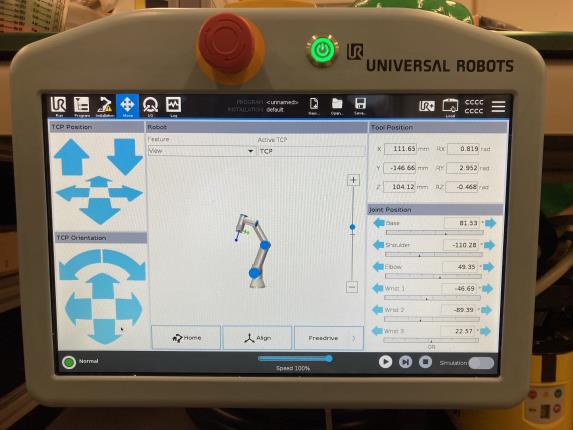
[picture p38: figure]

Figure 8: The Move screen has similar buton layouts for the CB (left) and E-Series teach pendants.

1. From the main menu, navigate to the “Move” screen (Fig. 8)
a. On the CB teach pendant: press the “Program robot” button, and select the “Move” tab at the top of the screen
b. On the E-Series teach pendant: select the “Move” tab at the top of the screen
2. At the bottom of the screen, the “Speed” adjuster modulates the maximum possible speed of the robot’s joints. By default, this is set to 100% (1000 mm/s)
3. On the left of the screen are Cartesian motion controls, where the coordinated motions of the joints are commanded in the Cartesian coordinate space relative to the base frame of the robot
a. The top-left window commands linear motions along the X, Y, and Z axes using the blue arrows
b. The bottom-left window commands rotations of the tool around the defined tool center point on the X, Y, and Z axes using the blue arrows
c. The current joint values and Cartesian position of the tool will be updated as the robot moves

4. Motions of the robot can also be commanded on a joint-by-joint basis by adjusting the joint sliders (or entering specfic angle values) in the Joint Position window (bottom of the screen on the CB teach pendant, or on the bottom-right of the screen on the E-Series teach pendant).
a. Pressing and holding the arrows will make the respective joints actuate, causing the robot to move
b. The current joint values and Cartesian position of the tool will be updated as the robot moves
c. The positive and negative extremes of the slider represent the maximum allowable motion limits for each joint. Attempting to move the robot beyond these limits will cause an error message regarding joint limits being met.
5. Pressing the field inputs for the tool position (white boxes with numbers) will cause a motion command window to appear in which specific joint values or Cartesian coordinates can be manually set
a. Specific values can be entered into each field directly using the on-screen keyboard
b. The orientation can be changed between an axis-angle (“rotation vector,” default) or Euler angle representation, in either radians (default) or degrees
c. Changes to these fields will not take effect until the “Okay” button is pressed
d. You will be asked whether you wish for the robot to move itself (“Auto”) or await user commands to move the robot to its commanded position (“Manual”)

### 4.3.2 Jogging Using the Freedrive Button

CAUTION: HEAT RISK

Freedriving the robot involves physically touching the robot. Robot joints and links may be hot due to extended use.

An alternative to using the Move screen is to leverage the robot’s gravity compensation (“Freedrive”) mode in which the tool and joints can be moved by the user physically pushing or pulling on the robot.

Freedrive does not require the user to be on a specific window or menu. To enable Freedrive, do the following:

1. With one hand, grasp the robot tool firmly, but do not push or pull on it. At this stage, you are merely supporting the weight of the robot in the event the tool mass and/or robot installation is not properly configured.
a. The tool will move downward if a tool mass larger than what it is expecting is present, or move upward if the tool mass is lower than what is expected
b. The tool may move rapidly in a random direction if the robot’s installation is not set properly. Review the UR manual for instructions of how to configure the installation.
2. With the other hand, press the black Freedrive button located at the top-center of the back of the teach pendant. This will release the brakes and the robot’s joints will move based on the user’s actions while holding onto the tool.
3. Gently push/pull/rotate the tooling to the desired pose, or adjust the joints individually to the desired configuration.
a. Pushing/pulling too hard, or attempting to move the joints too quickly may result in a safeguard fault. The resulting error screen must be cleared before Freedrive can be re-engaged.
b. The robot is monitoring and interpreting joint currents to effect pose changes based on its gravitational model, and is velocity-limited based on the set maximum speed. Larger payloads and/or lower maximum speeds may result in reduced responsiveness to user inputs.
4. Release the Freedrive button once the robot is in the desired position/configuration to disable Freedrive mode

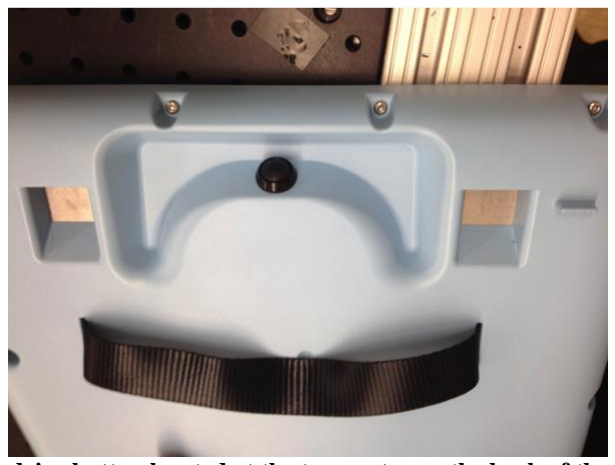
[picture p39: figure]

Figure 9: The Freedrive button located at the top-center on the back of the CB teach pendant.

## 5 Safety Verification Procedures

The required safety features shall be verified at the beginning of each month. The date and the signature of the authorized operator of the robot system performing the verification shall be entered in a log kept with the robot testbed.

### 5.1 Verify Robot Activation

1) Turn on the robot per Section 4.1
2) Visually verify that the power button on the teach pendant is illuminated and the screen is active
3) Initialize the robot per Section 4.2
4) Visually verify the robot is powered on and the drives are active
5) Turn off the robot (not the controller) by pressing the “OFF” button on the initialization screen of the CB teach pendant, or the power screen of the E-Series teach pendant.
6) Visually verify the robot’s power is OFF (drives are disabled and the joint motors are deenergized) and the brakes are engaged

### 5.2 Verify Local E-Stop

With the robot powered on:

1) Initialize the robot per Section 4.2
2) Visually verify the robot is powered on and the drives are activated
3) Press the emergency stop button on the teach pendant
4) Visually verify the teach pendant status
a) Message window displays the message, “EMERGENCY STOPPED”
5) Press the “Okay” (CB2) or “Go to initialization screen” (CB3 and E-Series) button to return to the initialization screen
6) Visually verify the teach pendant status
a) The robot status will indicate that it is “EMERGENCY STOPPED”
b) On the CB teach pendant: The “ON” button is disabled. The CB2 teach pendant will also give an individual joint status of “EMERGENCY STOPPED”
c) On the E-Series teach pendant: The “Start” button is disabled
7) Twist the E-Stop button on the teach pendant to release
8) Visually verify the teach pendant status
a) On the CB teach pendant:
i) Robot “ON” button is enabled
ii) Robot status is listed as “INITIALIZING”
iii) On the CB2 teach pendant, all joint status states listed as “READY”
b) On the E-Series teach pendant: Robot “Start” button is enabled
9) Initialize the robot per Section 4.2

### 5.3 Verify External E-Stop Buttons

With the robot powered on:

1) Initialize the robot per Section 4.2
2) Visually verify the robot is powered on and the drives are activated
3) Press the external E-Stop button
4) Visually verify the teach pendant status
a) Message window displays the message, “EMERGENCY STOPPED”
5) Press the “Okay” (CB2) or “Go to initialization screen” (CB3 and E-Series) button to return to the initialization screen
6) Visually verify the teach pendant status
a) The robot status will indicate that it is “EMERGENCY STOPPED”

b) On the CB teach pendant: The “ON” button is disabled. The CB2 teach pendant will also give an individual joint status of “EMERGENCY STOPPED”
c) On the E-Series teach pendant: The “Start” button is disabled
7) Twist the external E-Stop button to release
8) Visually verify the teach pendant status
a) On the CB teach pendant:
i) Robot “ON” button is enabled
ii) Robot status is listed as “INITIALIZING”
iii) On the CB2 teach pendant, all joint status states listed as “READY”
b) On the E-Series teach pendant: Robot “Start” button is enabled
9) Initialize the robot per Section 4.2

### 5.4 Verify Teach Pendant Functionality

With the robot powered on:

1) Initialize the robot per Section 4.2
2) Visually verify the robot is powered on and the drives are activated
3) Verify correctness of axes
a) Navigate to the move screen
b) Press and hold either the left or right arrow for each of the six joints separately; verify robot motion is correct and the values displayed are increasing/decreasing accordingly
c) Press and hold the robot move up or down arrow, verify direction of motion is correct
d) Press and hold the robot forward or backward arrow, verify direction of motion is correct
4) Verify Freedrive functionality
a) Press and hold the Freedrive button on the back of the teach pendant
b) Verify robot is not moving (if the robot moves up or down, the mass setting for the tool is too high or too low; if the robot moves in a different direction, the configuration settings for the installation of the robot are incorrect or one or more joints are experiencing errors in current monitoring)
c) Release the Freedrive button
d) Press and hold the Freedrive button
e) Gently grab and hold the tool or the tool flange
f) Attempt to push the robot upward, downward, and to the sides
g) Verify the robot’s direction of travel matches the direction you were pushing/pulling
h) Release the tool or tool flange
i) Gently push on any link or joint directly
j) Verify the robot’s direction of travel matches the direction you were pushing
k) Release the Freedrive button

## 6 Working Inside the Robot’s Work Volume

CAUTION: RISK OF STRUCK-BY AND PINCHING/CRUSHING HAZARDS

Personnel who must work within the robot’s work volume to perform, for example, set-up, installation, or troubleshooting tasks, shall be familiar with the basic workplace safety and robot safety. Personnel unfamiliar with workplace safety precautions (such as the use of safety glasses, and recognizing and eliminating trip hazards) should take the appropriate safety classes.

The following are the robot-specific safety precautions personnel should follow when working within the robot’s workzone:

1. Be familiar with the location of the robot E-Stop buttons for the robot testbed. The E-Stop buttons remove power from the robot drives and apply the brakes.
2. Before reaching inside the robot’s workzone, check to see if the robot controller is on and whether someone else is working with the robot. If someone is working with the robot, notify that person that you plan to work inside the robot workzone. Notify the person again if you plan to re-enter the robot workzone after a prolonged absence.
3. When not actively working with the robot, it is strongly recommended to leave the robot’s work volume, disable the robot, and/or activate an E-Stop button.

## 7 Programming Using the Teach Pendant

When possible, the operator should remain outside the robot’s work volume when teach programming with the pendant.

CAUTION: RISK OF STRUCK-BY AND PINCHING/CRUSHING HAZARDS

CAUTION: ERGONOMIC AND TRIPPING/FALL RISK

Programming using the teach pendant is typically done while holding the teach pendant. The weight of the teach pendant may cause ergonomic strain, and the cable connecting the teach pendant to the controller presents a tripping hazard.

### 7.1 Programming Outside the Robot Work Volume

The operator shall follow these steps when using the teach pendant outside the robot’s work volume. In situations where additional people are within the robot’s work volume during teach programming, it is the responsibility of the operator holding the teach pendant to notify personnel within the robot’s work volume that the robot is (or will be) on and to ensure that the robot does not hit or injure others.

1. Inform any personnel within the robot’s work volume that activities with the robot(s) are about to begin
2. Initialize the robot(s) per Section 4.2
3. Verify teach pendant functionality is working (see Section 5.4)
4. Proceed with programming. Be prepared to press the E-Stop button on the teach pendant if an imminent collision is observed or the robot’s behavior is not consistent with expected performance.

### 7.2 Programming Inside the Robot Work Volume

Sometimes it is necessary for the operator to enter the workzone for improved visibility and accessibility to the application. The operator shall follow these steps when using the teach pendant inside the work volume. In situations where additional people are inside the work volume during teach programming, it is the responsibility of the operator holding the teach pendant to notify personnel inside the work volume that the robot is on and to ensure that the robot does not hit or injure others.

1. Inform any personnel within the robot’s work volume that activities with the robot(s) are about to begin
2. Initialize the robot(s) per Section 4.2.
3. Verify teach pendant functionality is working (see Section 5.4)
4. Inform personnel present you are about to enter the robot’s work volume prior to entering.
5. Proceed with teach programming.
6. When done with tasks requiring presence inside the robot’s work volume, immediately exit the robot’s work volume.

## 8 Maintenance

Only authorized users shall conduct maintenance on the robot.

WARNING: RISK OF ELECTRICAL SHOCK WARNING: RISK OF HEAT/FIRE

Do not service the robot or its controler while powered.

Prior to any service or maintenance activity, the robot shall be actuated to a neutral position such that any potential energy in the system is minimized. The robot and its controller shall be de-energized prior to attempting to access the electrical and mechanical components.

Physically unplug the robot, the controller, and the safety system (if provided) to ensure that the robot is not re-energized inadvertently. After unplugging the equipment, allow the robot and controllers to sit for at least 30 minutes to allow for any residual charge in the systems’ capacitors to dissipate, and the equipment to cool to room temperature.

Refer to the appropriate robot service manuals for instructions for replacing/repairing components on the robot and controller.

## 9 Emergency Response Plan

### 9.1 Event: Equipment Fire

In the event of fire, immediately contact NIST Safety at x2222 to report the fire.

Authorized personnel may use an approved ABC fire extinguisher (combustible materials, flammable liquids, and flammable gases) to attempt to extinguish the fire. Acceptable fire extinguisher types include dry powder, alcohol-resistant foams, and carbon dioxide. An appropriate fire extinguisher must always be present in the same room as the robot, and all related personnel shall be informed of its location and trained in its use.

Do not use water to combat fires. Water may spread the flames and/or be insufficient for reducing temperatures of flammable materials below the flash point.

Do not resume use of the robot again until it has been inspected for damage that could negatively impact its safety.

### 9.2 Event: Forceful Impact with Human

Should accidental striking (i.e., non-constrained impact) occur with the robot, a held part (including one that may have been ejected from the robot’s gripper or pushed into contact with the operator), immediately move away from the robot and depress the E-Stop button.

Check all personnel for potential injuries such as cuts or bruising, contacting NIST Safety at x2222 if there has been an injury.

Reassess the activity’s hazard review—including the design of the working environment, the role of the operator in the activity, and selection of parts/tooling—to determine what controls can be added to prevent such events from occurring again.

Do not resume operations until the hazard has been mitigated.

### 9.3 Event: Crushing/Pinching

Keep hands and limbs away from crush/pinch points within the robot’s work volume while the robot is energized. Should accidental crushing/pinching occur:
- Immediately free the pinched/crush body part(s) away from the robot and move the impacted body part away from the robot when it is safe to do so.
- If the body part is pinned and extraction is not possible, attempt to jog the robot away from the body using Freedrive mode.
- If Freedrive mode cannot be enabled, individual joints may have their brakes released manually. To manually release a joint’s brakes, remove the blue plastic cover from the joint by removing the M3 screws. Press the plunger switch (see Fig. 10) to release the brakes.
- If the robot joints cannot be safely enabled to remove the risk state, or the brakes manually released, remove power from the robot by turning off the controller and unplugging it from the wall. With the power removed, the motors can be then safely back-driven. Alternatively, remove the four bolts connecting the robot to the mounting surface and move the robot away from the collision.

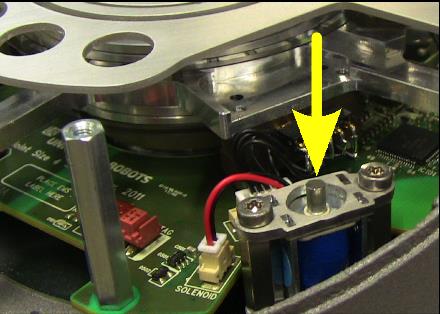
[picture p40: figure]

Figure 10: Brake release for an individual axis on the CB2 UR10.

Check all personnel for potential injuries such as cuts, bruising, or broken bones, contacting NIST Safety at x2222 if there has been an injury.

Power shall not be restored to the robot or its controller until physical access to all pinching/crushing hazards have been addressed with approved engineering controls.

### 9.4 Event: Contact with Forbidden Zones

Access of forbidden zones of the human body (e.g., head, face, or throat) to the mechanical and electrical parts inside the robot controller shall be prevented by safeguards at all times.

Should accidental contact occur, immediately move away from the robot, remove power from the robotic system, and disconnect the robot’s controller from the power source.

Check all personnel for potential injuries such as cuts or bruising, contacting NIST Safety at x2222 if there has been an injury.

Power shall not be restored to the robot or its controller until physical access to all moving components has been addressed with approved engineering controls.

### 9.5 Event: Robot Brake Failure

If the robot’s brakes fail while the robot is in operation, immediately remove power from the robot, and lock-out-tag-out the controller. The robot and its controller shall not be energized again until the robot has been serviced by an authorized service provider.

### 9.6 Event: Unexpected Robot Motion

Power fluctuations, unexpected/uncontrolled access to the robot’s network, controller errors, or unverified programs/inputs may result in the robot’s motions becoming erratic. If at any point the robot’s motions do not reflect what is expected:
- Immediately press the E-Stop button to halt all motions.
- Clear the error, and jog the robot to a known good configuration.
- If, while attempting to jog the robot, the unexpected robot motion manifests again, immediately press the E-Stop button and attempt to diagnose the issue with the robot controller. Having the robot be serviced by an authorized service provider may be required.
- Otherwise attempt to recreate the conditions under which the initial unexpected motions occurred, including any programs that might be running, external signals, or incurred forces/torques.
- If the unexpected robot motion manifests again, immediately press the E-Stop button and attempt to diagnose the root cause of the issue.

- If the robot itself (including motors, current monitors, and wiring) or its controller is the cause of the issue, disconnect power and have the robot serviced by an authorize service provider.
- If the robot program is the cause of the issue, attempt to debug the code in a controlled and safe manner.
- If the power supply is the cause of the issue (including external power inverters, wall power sockets, cables, power strips, and connectors) replace the effected components with known good alternatives and attempt to diagnose the source of the electrical fault.
- Otherwise resume normal operations, being certain to specifically watch for the unexpected motions to manifest again.

### 9.7 Event: Unplanned Release of Energy

The unexpected release of energy may present different hazards depending on the conditions in which the energy was released and the nature of the energy released.

### 9.7.1 Electrical

Immediately disconnect all power (including batteries) from the robot and any ancillary equipment. Check all personnel for potential impacts from ejected materials, or burns from live circuits or hot surfaces, contacting NIST Safety at x2222 if there has been an injury.

Do not attempt to restore power to the system until all power lines and grounds have been inspected and known to be intact and in proper working condition. Replace any damaged components or contacts showing wear or burning.

### 9.7.2 Pneumatic

An audible hissing will be heard if an air line or chamber ruptures, warning the operator and any nearby personnel that the structural integrity of the robot has failed. Immediately turn off and disconnect the air source, and remove power from the system. Check all personnel for potential impacts from ejected materials, contacting NIST Safety at x2222 if there has been an injury.

Do not attempt to restore power to the system until the ruptures have been permanently fixed, or the soft pneumatic lines have been replaced with new components.

Maintaining low air pressure in the system will dramatically reduce the risk of injury from ejected materials.

### 9.8 Event: Contact with Hot Parts of the Robot/Controller

Access to the mechanical and electrical parts inside the robot controller shall be prevented by safeguards. Should accidental contact occur, immediately remove power from the robotic system and disconnect the robot’s controller from the power source.

Check all personnel for potential injuries such as cuts or burns, contacting NIST Safety at x2222 if there has been an injury.

Power shall not be restored to the robot or its controller until physical access to all moving components has been addressed with approved engineering controls.

### 9.9 Building Related Hazards

### 9.9.1 Event: Fire

If a fire event occurs in the building and the building fire alarm sounds, immediately turn off any powered equipment, place any tools/parts on the floor in a safe and stable position, and then evacuate the building per NIST guidelines for building evacuation.

### 9.9.2 Event: Hazardous Weather

If a hazardous weather event occurs and the building alarm sounds, immediately turn off any powered equipment, place any tools/parts on the floor in a safe and stable position, and then move all personnel to the shelter-in-place zone in the building in a safe and orderly fashion.

### 9.9.3 Event: Power Outage

Activate the E-stop button for any robotic equipment that was previously powered, and turn off the power to any equipment operating under backup or battery power.

Move to a safe location away from any hazards until power has been restored.

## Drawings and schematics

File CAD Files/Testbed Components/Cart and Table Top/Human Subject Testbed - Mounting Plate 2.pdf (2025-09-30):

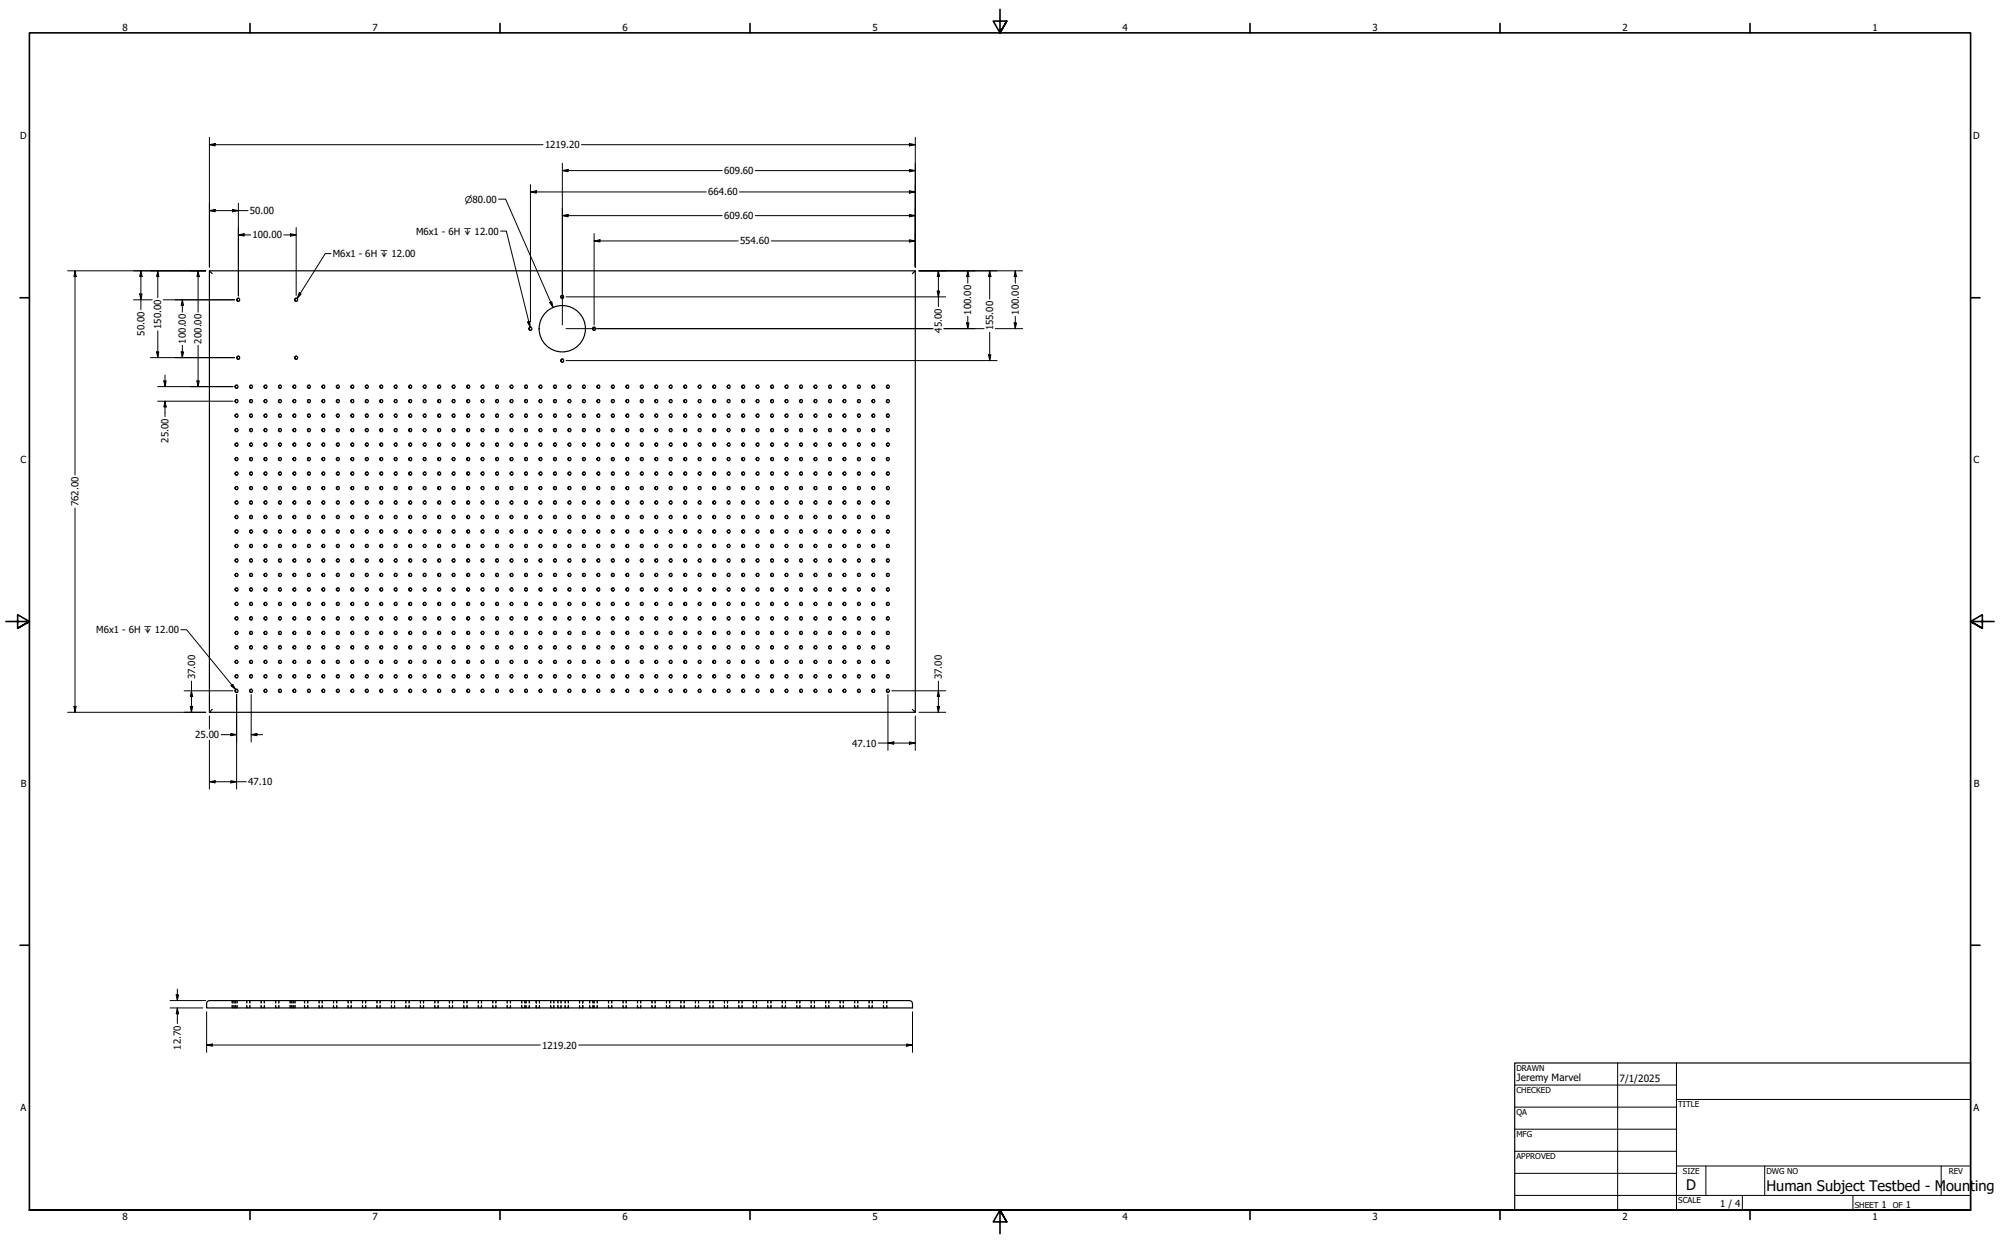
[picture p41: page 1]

DRAWN Jeremy Marvel | 7/1/2025

CHECKED

MFG

APPROVED

SIZE D | DWG NO | REV

Human Subject Testbed - Mounting P

SCALE 1 / 4 | | SHEET 1 OF 1

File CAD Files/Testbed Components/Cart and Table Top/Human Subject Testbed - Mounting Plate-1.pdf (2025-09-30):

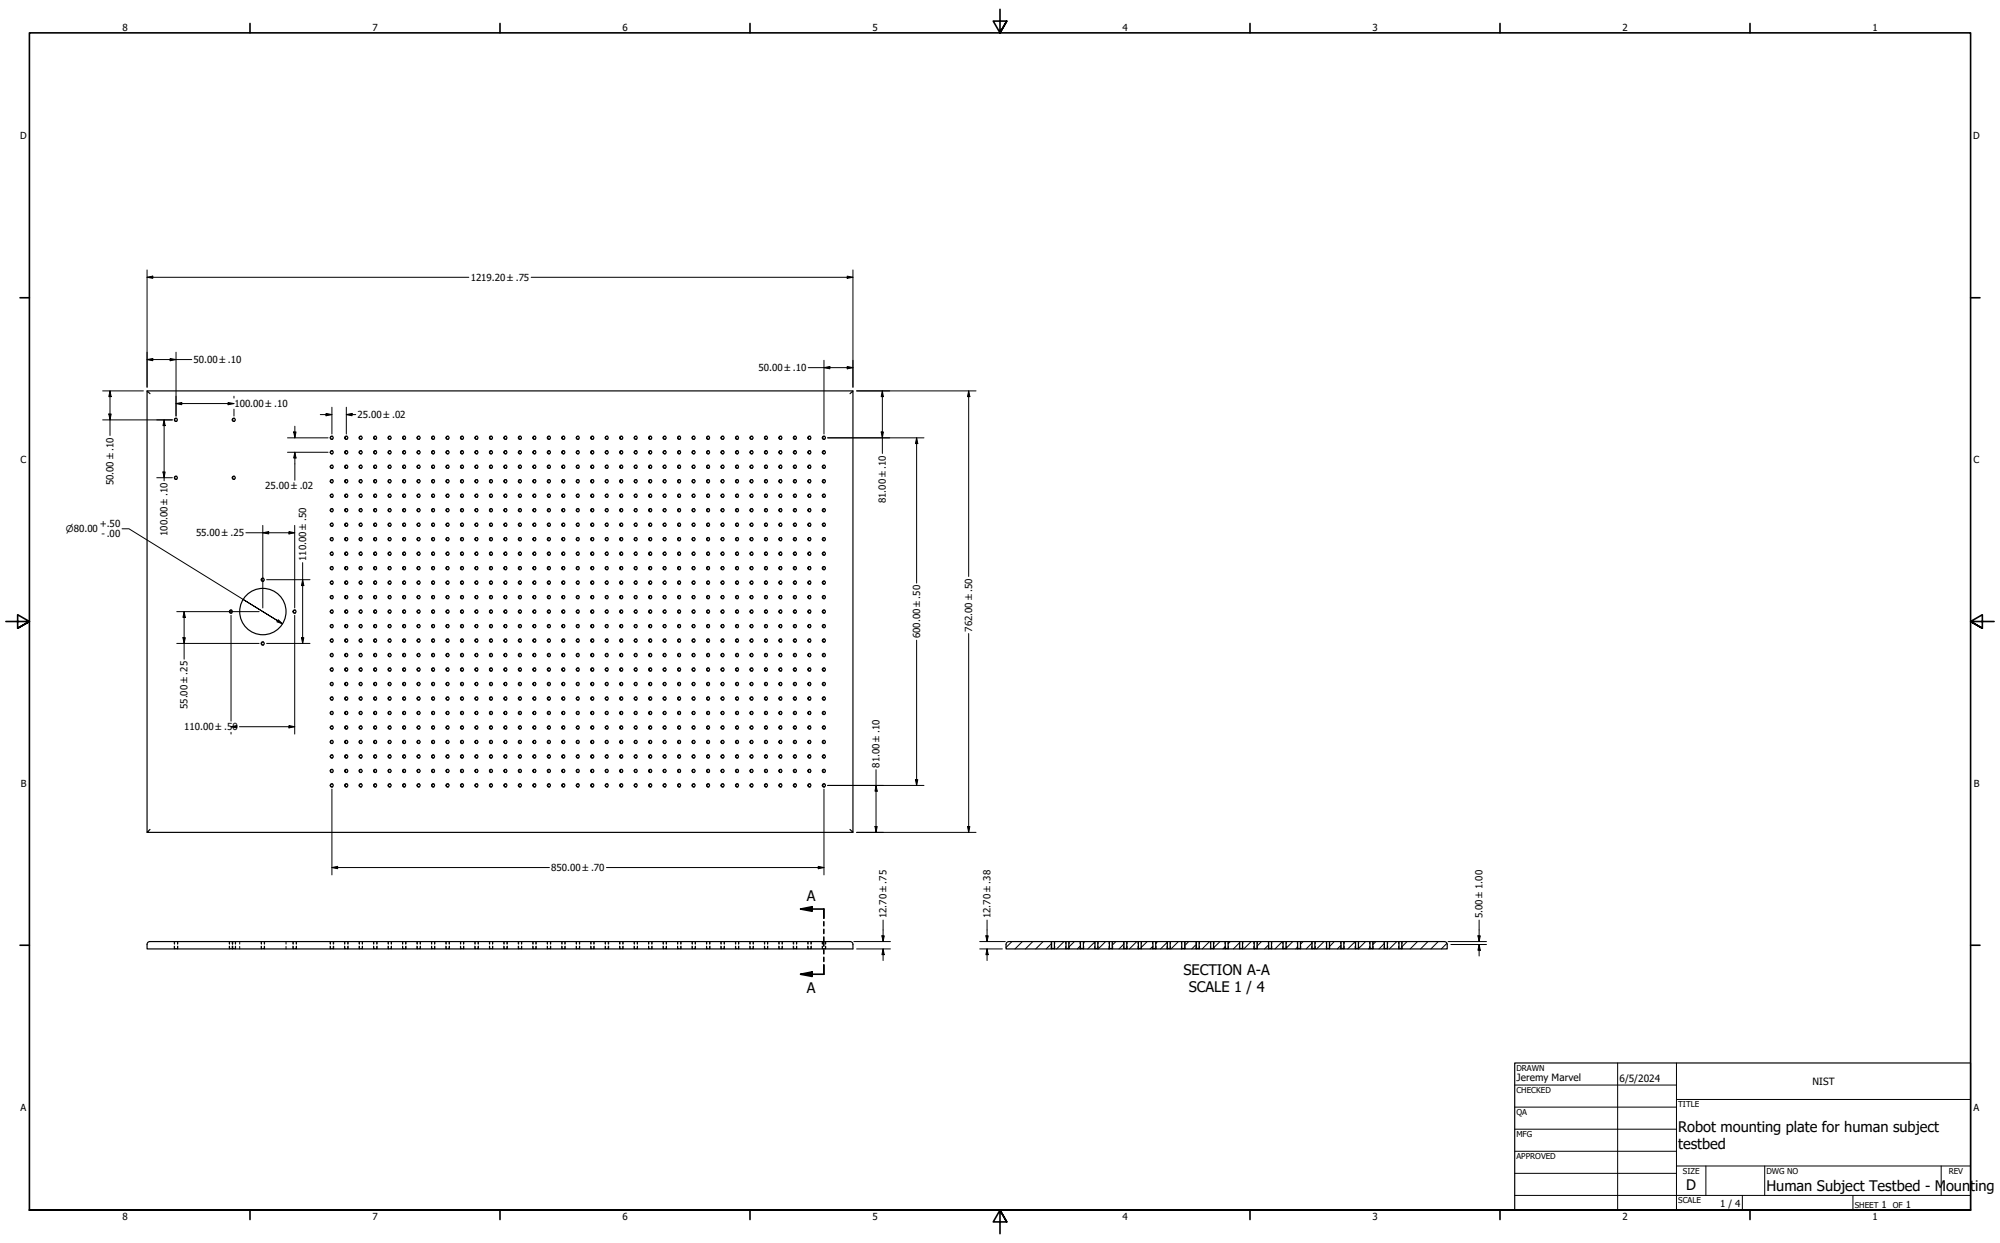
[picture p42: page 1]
SECTION A-A SCALE 1 / 4

DRAWN Jeremy Marvel | 6/5/2024 | NIST

CHECKED

TITLE
Robot mounting plate for human subject
testbed

MFG

APPROVED

SIZE D | DWG NO | REV

Human Subject Testbed - Mounting Plate-1

SCALE 1 / 4 | | SHEET 1 OF 1
